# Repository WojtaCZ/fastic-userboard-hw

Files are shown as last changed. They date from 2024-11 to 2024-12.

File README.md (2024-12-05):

# FastIC+ readout userboard
This repository contains the project files and manufacturing outputs for the FastIC+ readout userboard. The board can either be used with the [FastIC+ readout](https://github.com/WojtaCZ/fastic-readout-hw) as is or used as a template for development of a custom userboard compatible with the FastIC+ readout. 

<div align="center">
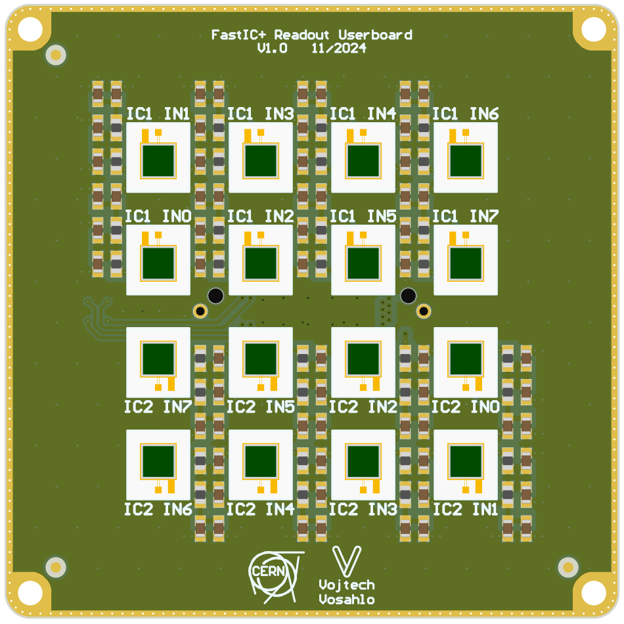
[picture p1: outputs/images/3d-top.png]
  
  
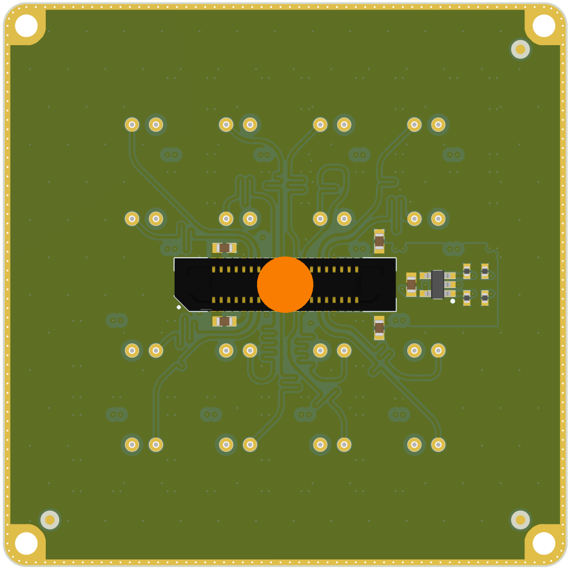
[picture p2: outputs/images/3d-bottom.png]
   
</div>

## Output files
Schematic, BOM and 3D renders are available in the outputs folder as well as the gerbers and pick and place files needed for assembly. Gerbers and P&P files for both a single board and a 2x2 panel are provided.

## Interface connector
The [ERF8-020-09.0-L-DV-K-TR](https://www.samtec.com/products/erf8-020-09.0-l-dv-k-tr) is used for interfacing with the readout system. The readout system provides a 3.3 V supply to the userboard on pins *40* and *39*. Decoupling capacitors should be added on these pins.

The identification pins *ID0*, *ID1*, *ID2* and *ID3* can be used for simple identification of the userboard by pulling them to 3.3 V or GND with a suitable resistor. The ID = 0b1111 (all pins are pulled high) is reserved to indicate that a I2C EEPROM is present on the board and available for configuration storage. *ID0* and *ID1* are than used for I2C communication with the EEPROM. The minimal EEPROM size is 4 kbit. **Note that the ID = 0b0000 (all pins pulled low) is reserved and cannot be used!**

High voltage for biasing of the sensors is provided by the readout system on pins *1*, *2*, *3* and *4*. Decoupling capacitors should be added on these pins.

The pins *INx_FASTICy* are input pins routed to the FastIC+ input channels. The channels on the readout board are length matched to provide consistent propagation delay for all channels.

<div align="center">
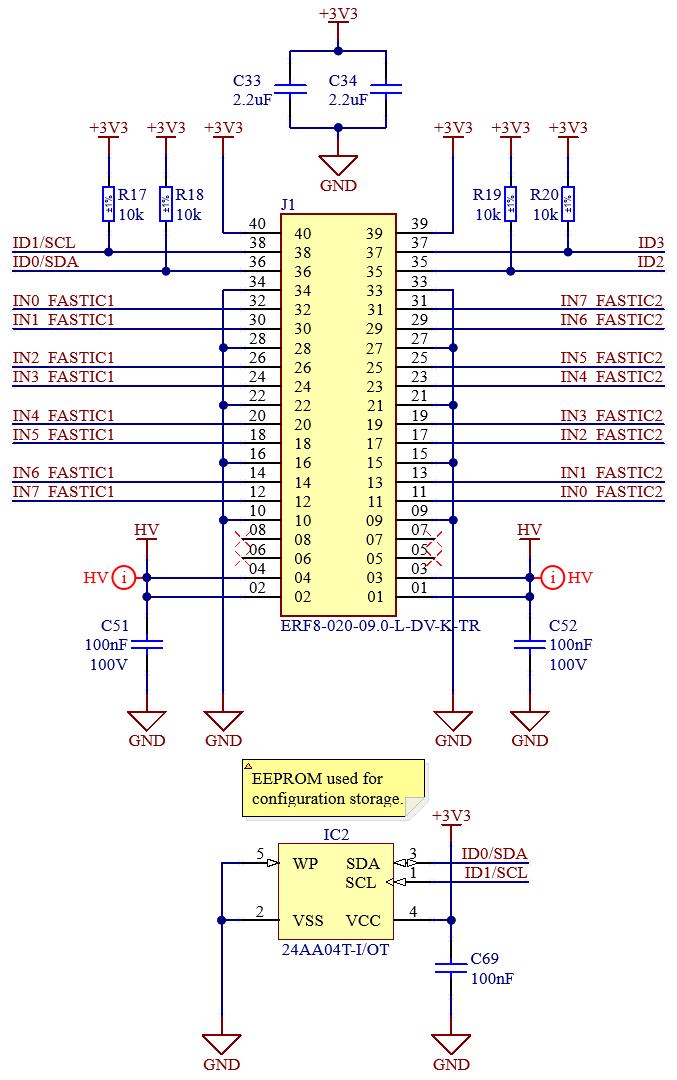
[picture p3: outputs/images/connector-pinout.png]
  
</div>

## Specifications
The following tables summarise the electrical specifications of the readout and userboard. These specifications need to be met in order to guarantee proper functionality.

The table bellow summarizes the currents and voltages that the readout can supply. 
<div align="center">

|                                        |   Min   |   Typ   |   Max   |   Unit   |
| -------------------------------------- | :-----: | :-----: | :-----: | :------: | 
| 3.3V voltage                           | 3.15    | 3.30    |  3.45   | V        |
| 3.3V current                           |         |         |  50     | mA       |
| HV voltage                             |         |         |  75     | V        |
| HV current                             |         |         |  5      | mA       |
| INx_FASTICy propagation delay[^1]      | 200     | 230     |  260    | ps       |

[^1]:
    The delay specified is the sum of the readout PCB propagation delay (120 ps) and the connector stack (mated connectors) propagation delay (110ps). The propagation delay of the FastIC+ package and the userboard PCB propagation delay is not taken into account. 

</div>
The following table than shows the parameters of the userboard.
<div align="center">

|                                        |   Min   |   Typ   |   Max   |   Unit   |
| -------------------------------------- | :-----: | :-----: | :-----: | :------: | 
| Pull resistor value                    | 10      |         |  100    | kOhm     |
| Channel propagation delay[^2]          | 110     | 140     |  170    | ps       |

[^2]:
    The channels in the provided user board example are length matched to (~ 140 ps), thus the total propagation delay from the sensor to the FastIC+ package pin is the sum of the user board delay (140 ps) and the propagation delay (230 ps), *t<sub>pd</sub> = 370 ± 30 ps*. The propagation delay of the FastIC+ package and the sensor propagation delay is not taken into account.

</div>

## List of compatible EEPROMs

<div align="center">

|              Manufacturer              |           Family          |          Example          |
| -------------------------------------- | :-----------------------: | :-----------------------: |
| Mircochip                              | 24AA series               | 24AA04T-I/OT              |

</div>

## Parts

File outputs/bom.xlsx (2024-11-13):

Name | Voltage | Case | Description | Designator | Quantity | Manufacturer 1 | Manufacturer Part Number 1 | Manufacturer Lifecycle 1 | Supplier 1 | Supplier Part Number 1 | Supplier Order Qty 1 | Supplier Stock 1 | Supplier Unit Price 1 | Supplier Subtotal 1 | Fitted
2.2uF | 10V | 0603 | Non-polarised capacitor | C33, C34 | 2 | Murata | GRM188R71A225KE15D | Volume Production | Mouser | 81-GRM188R71A225KE15 | 100 | 63543 | 0.0395 | 3.95 | Yes
10k |  | 0402 | Resistor - 1% | R17, R18, R19, R20 | 4 | Yageo | RC0402FR-0710KL | Volume Production | Digikey | 311-10.0KLRDKR-ND | 160 | 7379105 | 0.00386 | 0.617 | Yes
24AA04T-I/OT |  | SOT23-5 | 1.7V-5.5V, 16K I2C Serial EEPROM | IC2 | 1 | Microchip | 24AA04T-I/OT | Volume Production | Digikey | 24AA04T-I/OTCT-ND | 40 | 6698 | 0.26147 | 10.46 | Yes
49R9 |  | 0603 | Resistor - 1% | R1, R2, R3, R4, R5, R6, R7, R8, R9, R10, R11, R12, R13, R14, R15, R16, R21, R22, R23, R24, R25, R26, R27, R28, R29, R30, R31, R32, R33, R34, R35, R36 | 32 | Yageo | RT0603BRD0749R9L | Volume Production | Rs | 1991558 | 1280 | 2670 | 0.03414 | 43.7 | Yes
100nF | 100V | 0603 | Non-polarised capacitor | C1, C2, C3, C4, C5, C6, C7, C8, C9, C10, C11, C12, C13, C14, C15, C16, C17, C18, C19, C20, C21, C22, C23, C24, C25, C26, C27, C28, C29, C30, C31, C32, C35, C36, C37, C38, C39, C40, C41, C42, C43, C44, C45, C46, C47, C48, C49, C50, C51, C52, C53, C54, C55, C56, C57, C58, C59, C60, C61, C62, C63, C64, C65, C66, C67, C68, C69 | 67 | TDK | CGA3E3X7S2A104K080AB | Volume Production | Arrow Electronics | CGA3E3X7S2A104K080AB | 4000 | 76000 | 0.01909 | 76.37 | Yes
ERF8-020-09.0-L-DV-K-TR |  |  |  | J1 | 1 | Samtec | ERF8-020-09.0-L-DV-K-TR | Volume Production | Digikey | 612-ERF8-020-09.0-L-DV-K-TRCT-ND | 40 | 362 | 4.79 | 191.41 | Yes
S13360-3050CS |  |  | Single Element MPPC (Multi-Pixel Photon Counter) | IC1, IC3, IC4, IC5, IC6, IC7, IC8, IC9, IC10, IC11, IC12, IC13, IC14, IC15, IC16, IC17 | 16 |  |  |  |  |  |  |  |  |  | No
Use only in PCB |  |  | Fiducial Target | FTG1, FTG2, FTG3, FTG4, FTG5, FTG6 | 6 |  |  |  |  |  |  |  |  |  | No

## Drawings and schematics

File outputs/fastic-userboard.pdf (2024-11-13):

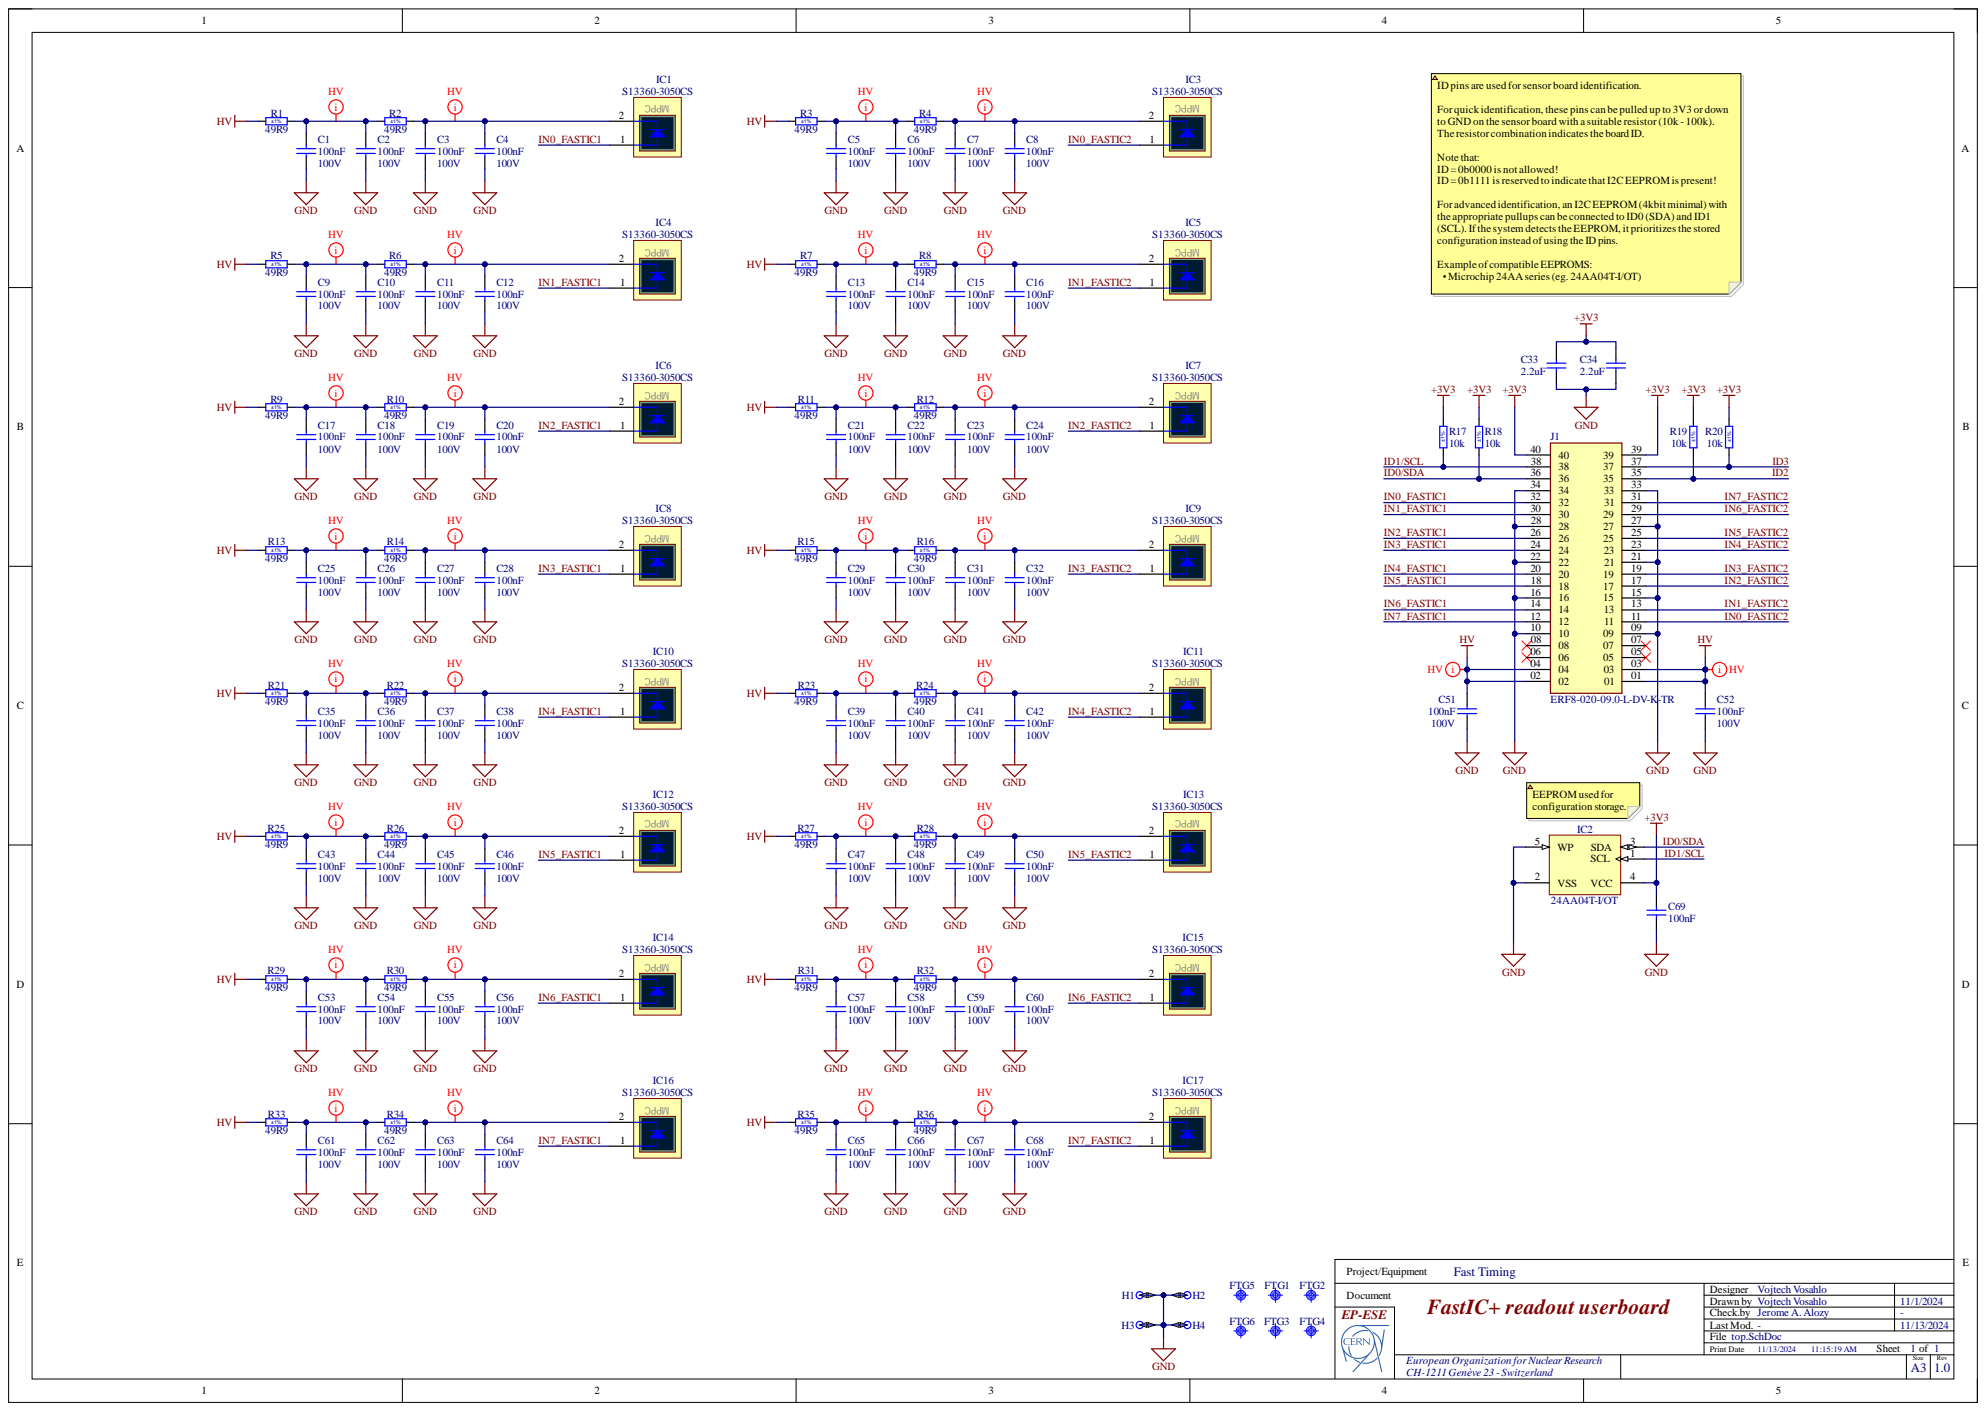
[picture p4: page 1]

ID pins are used for sensor board identification.

For quick identification, these pins can be pulled up to 3V3 or down
to GND on the sensor board with a suitable resistor (10k - 100k).
The resistor combination indicatesthe board ID.

Note that:
ID = 0b0000 is not allowed!
ID = 0b1111 isreserved to indicate thatI2C EEPROM is present!

For advanced identification, an I2C EEPROM (4kbit minimal) with
the appropriate pullups can be connected to ID0 (SDA) and ID1
(SCL). If the system detectsthe EEPROM, it prioritizesthe stored
configuration instead of using the ID pins.

Example of compatible EEPROMS:
•Microchip 24AAseries(eg. 24AA04T-I/OT)

Designer Vojtech Vosahlo
Drawn by Vojtech Vosahlo
Check.by Jerome A. Alozy
Last Mod. -
top.SchDoc
Print Date

European Organization forNuclear Research
CH-1211 Genève 23 - Switzerland

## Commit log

2024-11-13 Updated images
    [fastic-userboard.PrjPcb]
2024-11-28 Added panel files
    [fastic-userboard.PcbDoc, fastic-userboard_PANEL.PcbDoc, pick-and-place.csv]
2024-11-28 Added 3D files
    [fastic-userboard.PrjPcb]
